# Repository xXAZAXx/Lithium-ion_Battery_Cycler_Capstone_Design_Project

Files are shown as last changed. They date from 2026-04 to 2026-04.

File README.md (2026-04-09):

# Lithium-ion_Battery_Cycler_Capstone_Design_Project
Designed and developed a low-cost automated single-cell lithium-ion battery cycler for controlled charge and discharge testing. The system integrates a custom PCB, microcontroller-based control, and real-time data acquisition using Python and MATLAB for visualization and analysis.

### Assembled PCB Hardware
The completed, soldered PCB used for the battery cycler system.

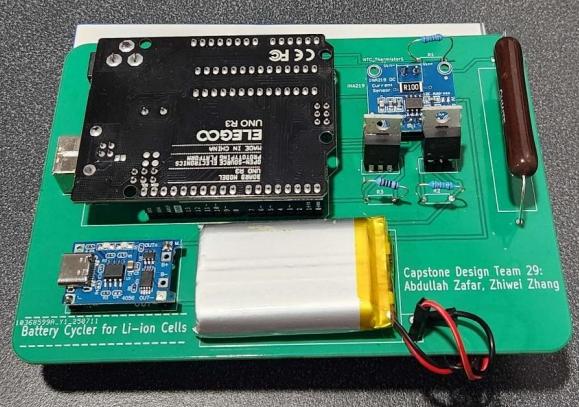
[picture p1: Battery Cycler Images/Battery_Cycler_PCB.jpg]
Assembled PCB


---

### PCB Schematic & 3D Render (KiCad)
Schematic and 3D render showing component placement and overall hardware design.

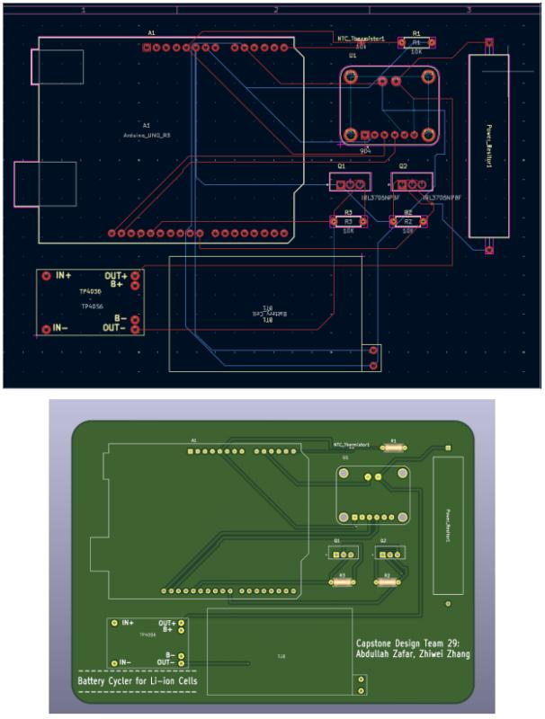
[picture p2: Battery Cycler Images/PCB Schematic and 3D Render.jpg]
PCB Design


---

### MATLAB Standalone Application 
Custom MATLAB App Designer interface used for real-time visualization and analysis of charge/discharge data.

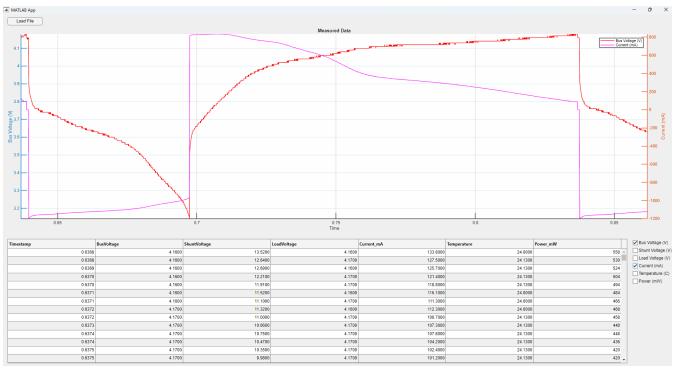
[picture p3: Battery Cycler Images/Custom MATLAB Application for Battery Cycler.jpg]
Custom MATLAB Application

---

## Technologies Used
- **Embedded Systems:** Arduino / Microcontroller-based control  
- **Programming:** Python, MATLAB  
- **Hardware Design:** KiCad (PCB Design & Layout)  
- **Data Processing:** CSV logging, real-time plotting (Matplotlib / MATLAB)  

---

## Results
The system enables reliable and repeatable charge/discharge testing of lithium-ion cells, with real-time monitoring and post-processing for performance evaluation.

---

## Note
This project was developed as part of a fourth-year capstone design project at the University of Windsor.

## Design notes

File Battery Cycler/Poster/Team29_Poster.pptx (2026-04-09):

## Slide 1

Team 29: Battery Cycler for Lithium-Ion Cells

Team Member: Abdullah Zafar, Zhiwei Zhang
Faculty Advisor: Dr. Chunhong Chen

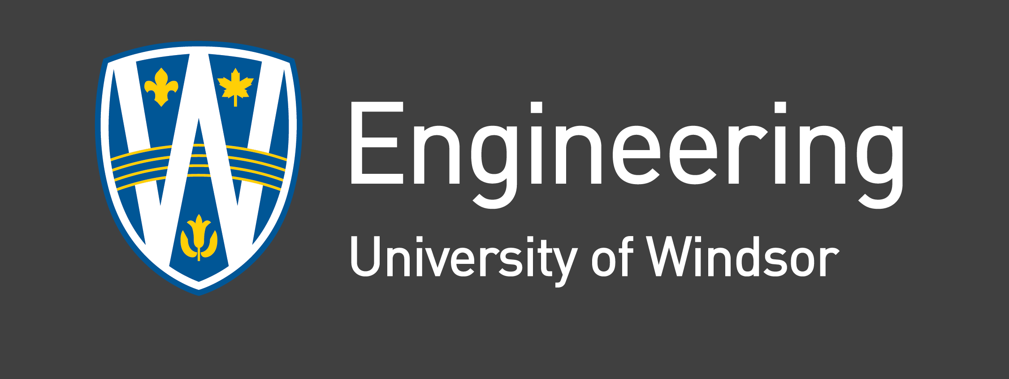
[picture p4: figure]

Department of Electrical and Computer Engineering
Capstone 2025: Team #29
July 25th, 2025

Hardware Subsystem: A compact cycling circuit built around the Arduino UNO, including:
- Charging and discharging switching using two logic-level N-channel MOSFETs (IRL3705NPBF)
- INA219 current sensor for current, and power monitoring
- TP4056 charging module with a 3.7V 1600mAh Li-ion battery
- 3Ω, 10W power resistor to serve as the discharge load
- NTC thermistor and DHT11 sensors to track battery and ambient temperature.
- All components are soldered on prototype boards using 22 AWG wiring for safe current handling.
Control Interface: Features an LCD screen and a two-button system for manual control:
- Button 1: Activates charging mode
- Button 2: Activates discharging mode
- Both buttons held together: Puts the system into standby mode
- A long press toggles LCD views between electrical and environmental data
Software Subsystem: Cycle control & data logging
- Arduino firmware to read sensors, control states, and update the display
- Python script for real-time serial data logging in CSV format
- MATLAB for post-processing and visual analysis of logged data

Experimental Result

During charging, the voltage increased from ~3.6V to 4.2V while current gradually decreased, the general trend shows expected constant-current and constant-voltage behaviour of a Li-ion cell. Upon reaching full charge, the system automatically transitioned to discharging mode. Voltage then steadily declined as the battery discharged with current remaining relatively constant around 120–150 mA.

Abstract

This project aims to create a low-cost automated battery cycler for testing single-cell lithium-ion batteries. It offers an affordable alternative to expensive commercial testers, making battery research more accessible to students and smaller labs. The system uses an Arduino UNO, INA219 sensor, TP4056 charging module, and logic-level MOSFETs, to control and monitor charging and discharging cycles. Voltage, current, power and temperature are measured in real-time, with data streamed to Python for datalogging and later analyzed using MATLAB.

Introduction

This project addresses the high cost of battery testing by developing a low-cost, automated battery cycler using widely available components. The current state-of-the-art in battery testing offer multi-channel, high-precision control, but cost thousands of dollars and are out of reach to students, and small-scale researchers. Our solution repurposes an Arduino UNO, INA219 current sensor, NTC thermistor, TP4056 charging module, and logic-level MOSFETs into a reliable, single-cell battery cycler. It automates the charging and discharging process while measuring voltage, current, power, and temperature in real-time. Data is streamed and logged via Python, then analyzed using MATLAB to provide professional-quality results. By utilizing low-cost components and open-source tools, this project provides a practical and scalable alternative to commercial testers, so battery research and testing can be done on a budget.

Deliverables

In this project, we intend to demonstrate the functionality of a battery cycling system designed, shown below, capable of automated charging and discharging of a single-cell lithium-ion battery.
The complete
system includes
both hardware
and software
components
designed to
operate in
real-time and
provide battery
performance insights.

Figure 1. Battery Cycler Circuit Schematic

Figure 3. Discharging Cycle Data

Conclusions

The battery cycler met its performance goals by successfully automating charge/discharge cycles and the measured performance aligned with expected lithium-ion behaviour. Showing a stable constant-current and constant-voltage charging profile, and consistent current during discharge. The prototype achieved accurate real-time data logging and control using low-cost components. Its key innovation is demonstrated by offering a reliable, affordable alternative to commercial testers through open-source hardware and software integration.

Future Work

Future work can focus on full PCB integration. While the current version relies on modules, we have already designed a PCB around them. The next step is to transition to a fully integrated design using I²C for improved compactness and reliability. Additional upgrades could also include SoC estimation and multi-cell support with cell balancing to move closer to a commercial-grade battery testing solution.

Acknowledgement

With utmost gratitude to Dr. Chunchong Chen for his guidance, and special thanks to Tony Fuerth & Tim Bolger

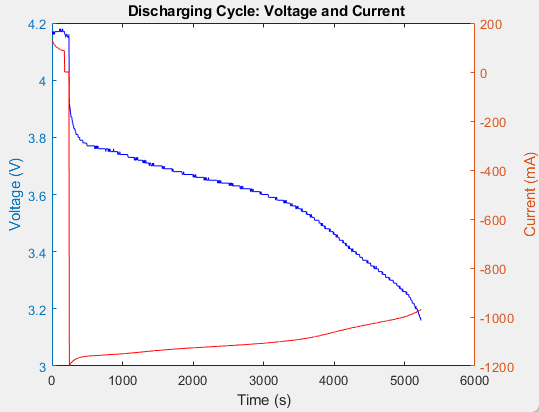
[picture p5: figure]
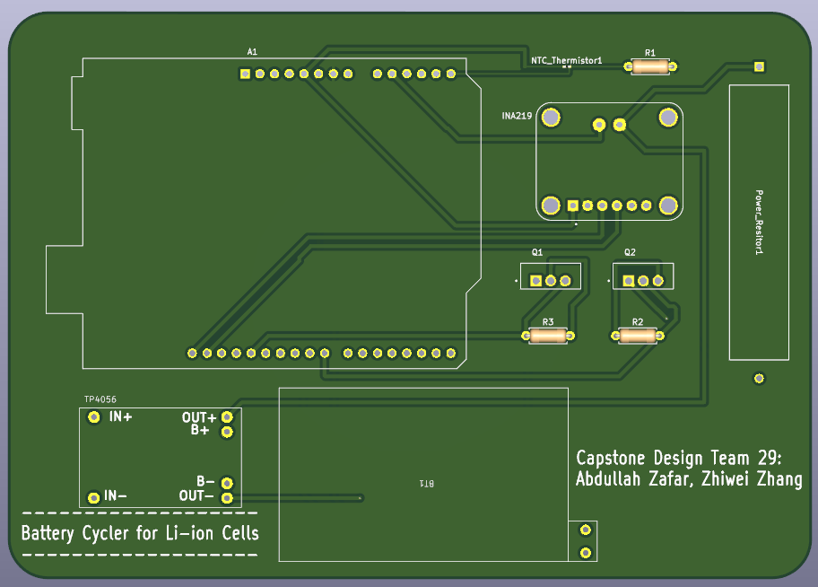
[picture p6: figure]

Figure 4. PCB Schematic

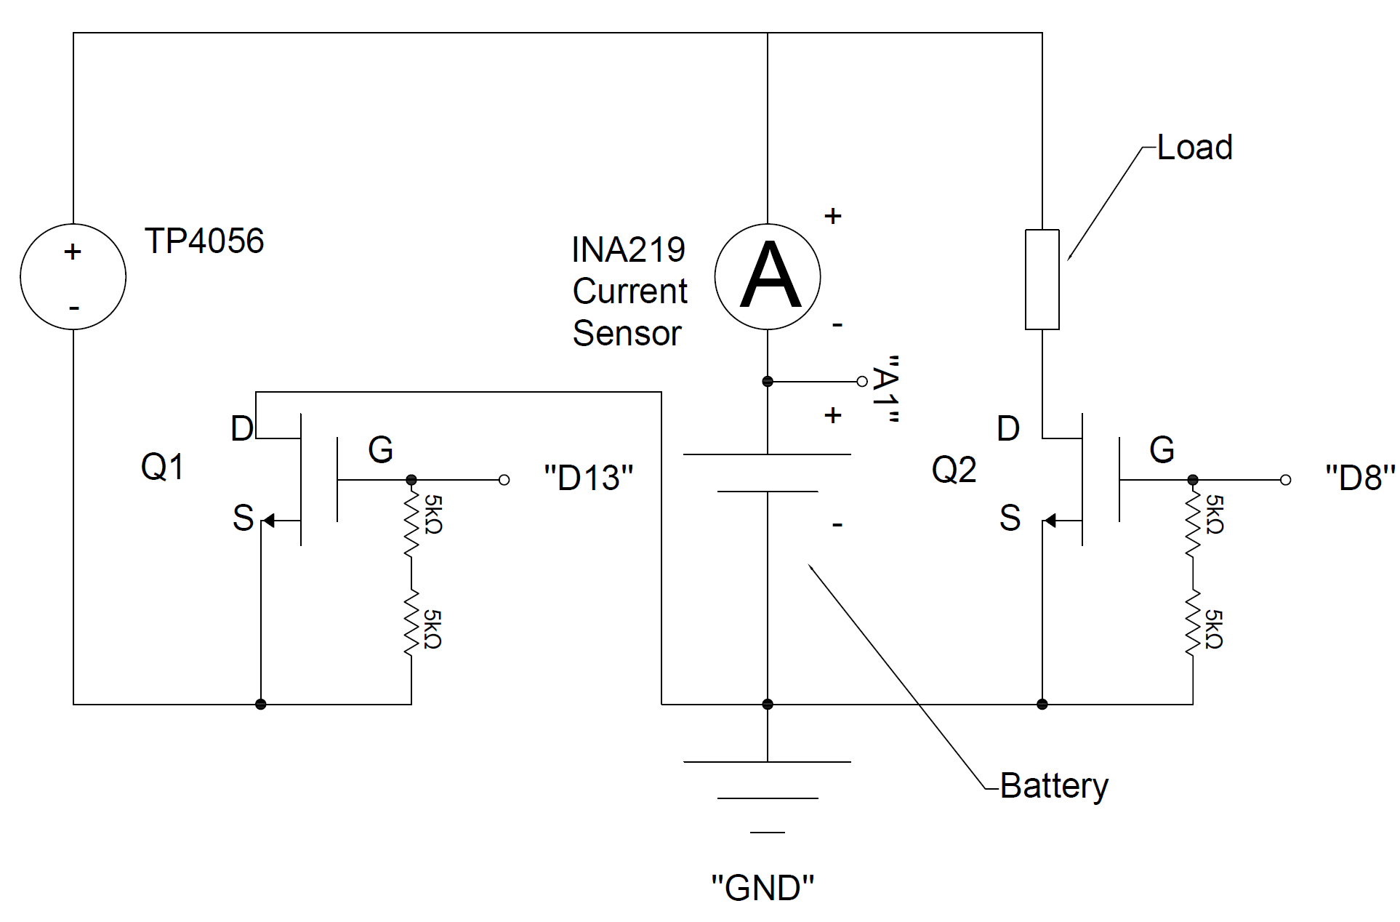
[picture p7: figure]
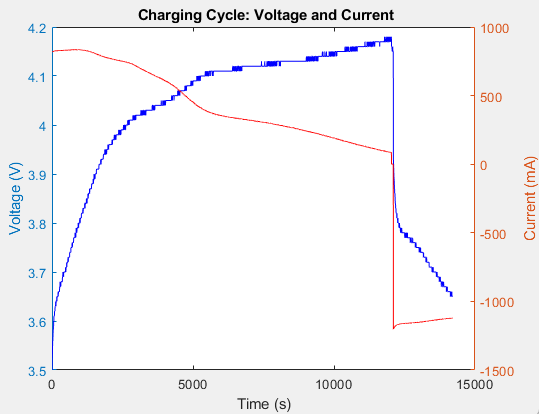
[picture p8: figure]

Figure 2. Charging Cycle Data

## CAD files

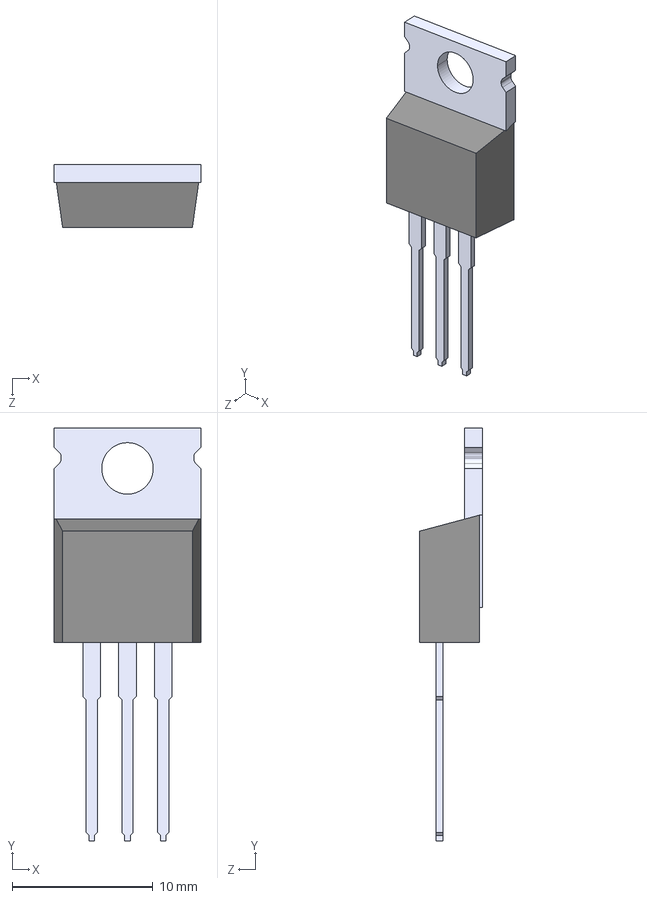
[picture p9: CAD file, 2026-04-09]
Battery Cycler/AZ_PCB_Capstone/IRL3705NPBF/IRL3705NPBF.step
10.4 x 29.3 x 4.45 mm

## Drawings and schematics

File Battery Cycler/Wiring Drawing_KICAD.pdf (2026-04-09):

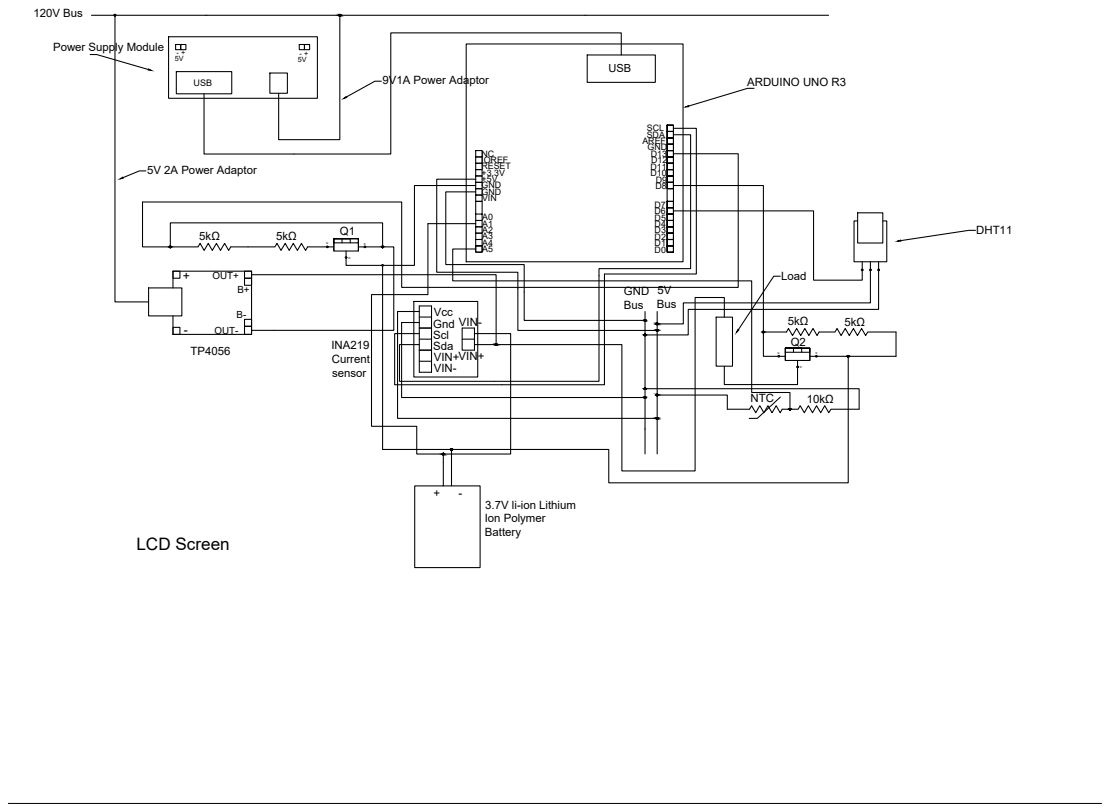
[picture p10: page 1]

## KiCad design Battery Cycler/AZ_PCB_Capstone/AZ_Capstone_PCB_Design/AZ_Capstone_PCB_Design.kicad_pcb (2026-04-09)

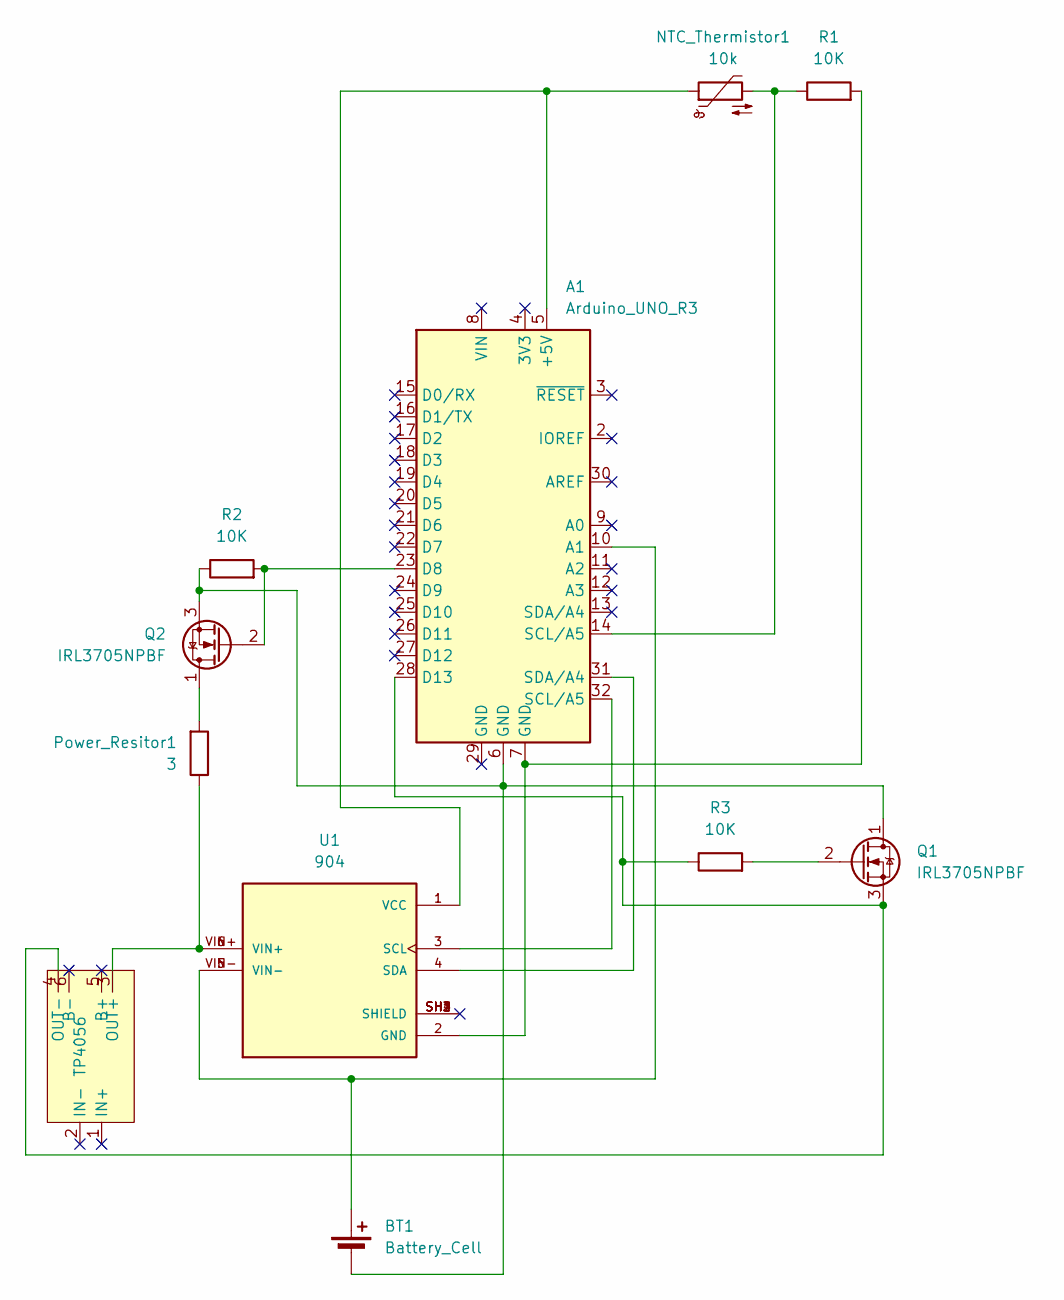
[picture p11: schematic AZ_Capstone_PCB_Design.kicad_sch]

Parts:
A1: Arduino_UNO_R3
BT1: Battery_Cell; 103048 Li-ion Polymer Battery
NTC_Thermistor1: 10k; R_0201_0603Metric_Pad0.64x0.40mm_HandSolder; Part No. MF51E103F3950
Power_Resitor1: 3; RES_20_OHM; Part No. 20J3R0E-ND
Q1, Q2: IRL3705NPBF; TO254P1041X444X1930-3; Part No. IRL3705NPBF
R1, R2, R3: 10K; R_Axial_DIN0207_L6.3mm_D2.5mm_P7.62mm_Horizontal
TP4056: TP4056-MODULE-AZ
U1: 904; MODULE_904; PARTREV C

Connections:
unnamed 0: A1.5 (+5V), NTC_Thermistor1.1, U1.1 (VCC); also elsewhere on the board
unnamed 1: A1.10 (A1), BT1.1 (+), U1.5 (VIN-), U1.VIN-; also elsewhere on the board
unnamed: A1.23 (D8), Q2.2 (G), R2.2
unnamed: A1.28 (D13), Q1.3 (S), R3.1, TP4056.4 (OUT-)
unnamed: A1.14 (SCL/A5), NTC_Thermistor1.2, R1.1
unnamed: A1.6 (GND), BT1.2 (-), Q1.1 (D), Q2.3 (S), R2.1
unnamed: Q1.2 (G), R3.2
unnamed: Power_Resitor1.2, Q2.1 (D)
unnamed 8: Power_Resitor1.1, TP4056.3 (OUT+), U1.6 (VIN+), U1.VIN+; also elsewhere on the board
unnamed 9: A1.7 (GND), R1.2, U1.2 (GND); also elsewhere on the board
unnamed: U1.SH1 (SHIELD), U1.SH2 (SHIELD), U1.SH3 (SHIELD), U1.SH4 (SHIELD)
unnamed 11: A1.32 (SCL/A5), U1.3 (SCL); also elsewhere on the board
unnamed 12: A1.31 (SDA/A4), U1.4 (SDA); also elsewhere on the board

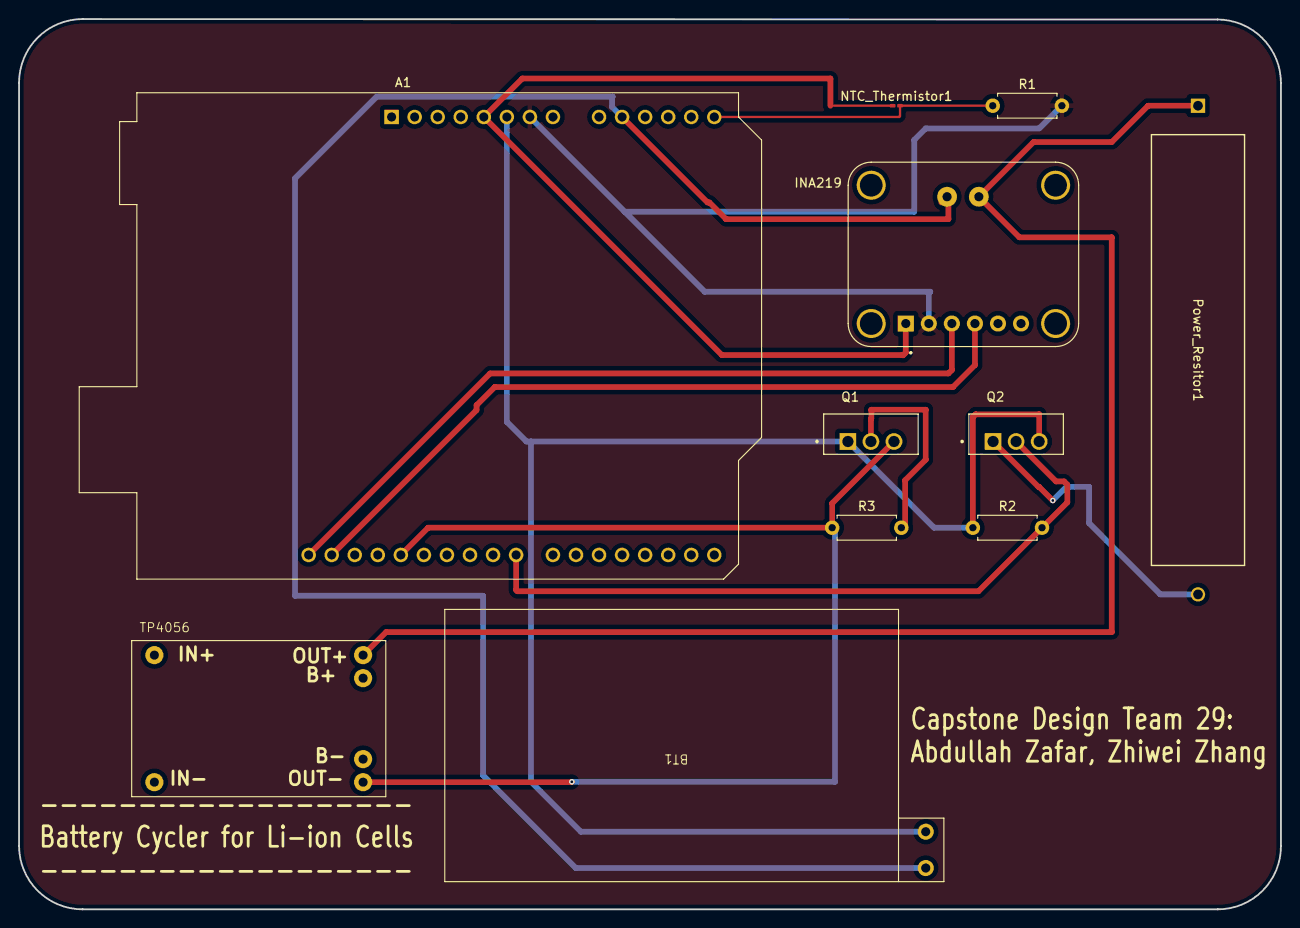
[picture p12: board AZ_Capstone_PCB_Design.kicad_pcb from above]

Board: 2 copper layers, 139.1 x 98.1 mm, 11 parts (0 on the bottom side), 13 nets.

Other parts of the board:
INA219: 904; MODULE_904

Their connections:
unnamed 0: INA219.1 (VCC); also elsewhere on the board
unnamed 1: INA219.5 (VIN-), INA219.VIN-; also elsewhere on the board
unnamed 8: INA219.6 (VIN+), INA219.VIN+; also elsewhere on the board
unnamed 9: INA219.2 (GND); also elsewhere on the board
unnamed 11: INA219.3 (SCL); also elsewhere on the board
unnamed 12: INA219.4 (SDA); also elsewhere on the board
unnamed: INA219.SH1 (SHIELD), INA219.SH2 (SHIELD), INA219.SH3 (SHIELD), INA219.SH4 (SHIELD)

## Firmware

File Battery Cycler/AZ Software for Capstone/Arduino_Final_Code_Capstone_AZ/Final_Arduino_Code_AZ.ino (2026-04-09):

#include <Wire.h>
#include <Adafruit_INA219.h>
#include <LiquidCrystal.h>
#include <math.h>

Adafruit_INA219 ina219;

// LCD pins: rs, en, d4, d5, d6, d7
const int rs = 12, en = 11, d4 = 5, d5 = 4, d6 = 3, d7 = 2;
LiquidCrystal lcd(rs, en, d4, d5, d6, d7);

bool button1 = 0;
bool button2 = 0;
bool button3 = 0;

bool LCD_state = 0;
bool charging_state = 0;
bool discharging_state = 0;

int Vo;
float R1 = 10000;
float logR2, R2, T, Tc;
float c1 = 1.009249522e-03, c2 = 2.378405444e-04, c3 = 2.019202697e-07;

// Auto switching control
unsigned long lowVoltageStart = 0;
unsigned long lowCurrentStart = 0;
const unsigned long switchDelay = 60000; // 1 minute
const float MIN_VOLTAGE = 3.2;
const float MIN_CURRENT = 1.0;
const float MIN_VOLTAGE_FOR_FULL = 4.13;

void setup() {
  pinMode(13, OUTPUT);  // Charging gate
  pinMode(8, OUTPUT);   // Discharging gate
  pinMode(10, INPUT);   // Button2: manual charging
  pinMode(9, INPUT);    // Button3: manual discharging
  pinMode(7, INPUT);    // Button1: LCD toggle

  Serial.begin(115200);
  while (!Serial) { delay(1); }

  if (!ina219.begin()) {
    Serial.println("Failed to find INA219 chip");
    while (1) { delay(10); }
  }

  ina219.setCalibration_32V_2A();
  lcd.begin(16, 2);
  lcd.clear();
}

void loop() {
  // --- Sensor Readings ---
  float shuntvoltage = ina219.getShuntVoltage_mV();
  float busvoltage = ina219.getBusVoltage_V();
  float current_mA = ina219.getCurrent_mA();
  float power_mW = ina219.getPower_mW();
  int sensorValue = analogRead(A1);
  float loadvoltage = (sensorValue * 5.0) / 1023;

  button2 = digitalRead(10);
  button3 = digitalRead(9);
  button1 = digitalRead(7);

  // --- Manual Controls ---
  if (button2 == 1) {
    charging_state = 1;
    discharging_state = 0;
  }
  if (button3 == 1) {
    charging_state = 0;
    discharging_state = 1;
  }

  unsigned long now = millis();

  // --- Auto Switching Logic ---
  // Start charging if voltage too low
  if (loadvoltage <= MIN_VOLTAGE) {
    if (lowVoltageStart == 0) lowVoltageStart = now;
    if (now - lowVoltageStart >= switchDelay) {
      charging_state = 1;
      discharging_state = 0;
    }
  } else {
    lowVoltageStart = 0;
  }
  // Start discharging if current is very low and voltage is high (battery full)
  if (charging_state == 1 && current_mA <= MIN_CURRENT && loadvoltage >= MIN_VOLTAGE_FOR_FULL) {
    if (lowCurrentStart == 0) lowCurrentStart = now;
    if (now - lowCurrentStart >= switchDelay) {
      discharging_state = 1;
      charging_state = 0;
    }
  } else {
    lowCurrentStart = 0;
  }

  // --- Actuate Charge/Discharge Gates ---
  digitalWrite(13, charging_state ? HIGH : LOW);
  digitalWrite(8, discharging_state ? HIGH : LOW);

  // --- Thermistor Temperature Calculation ---
  Vo = analogRead(A5);
  R2 = R1 * (1023.0 / (float)Vo - 1.0);
  logR2 = log(R2);
  T = (1.0 / (c1 + c2 * logR2 + c3 * pow(logR2, 3)));
  Tc = T - 273.15 - 22;  // Adjusted calibration offset

  // --- LCD Real-Time Display ---
  lcd.setCursor(0, 0);
  lcd.print("I:");
  lcd.print(current_mA, 1);
  lcd.print("mA ");

  lcd.setCursor(10, 0);  // Status on top-right
  if (charging_state) {
    lcd.print("C ");
  } else if (discharging_state) {
    lcd.print("D ");
  } else {
    lcd.print("  ");  // Clear if neither
  }

  lcd.setCursor(0, 1);
  lcd.print("V:");
  lcd.print(loadvoltage, 2);
  lcd.print("V ");

  lcd.print(Tc, 1);
  lcd.print((char)223);
  lcd.print("C ");

  // --- Serial Output for Python Logging ---
  Serial.print("BusVoltage:"); Serial.print(busvoltage); Serial.print("\t");
  Serial.print("ShuntVoltage:"); Serial.print(shuntvoltage); Serial.print("\t");
  Serial.print("LoadVoltage:"); Serial.print(loadvoltage); Serial.print("\t");
  Serial.print("Current_mA:"); Serial.print(current_mA); Serial.print("\t");
  Serial.print("Temperature:"); Serial.print(Tc); Serial.print("\t");
  Serial.print("Power_mW:"); Serial.println(power_mW);
  //delay(5000); // Log every 5 seconds
 // delay(1000); // Log every 1 seconds
}
